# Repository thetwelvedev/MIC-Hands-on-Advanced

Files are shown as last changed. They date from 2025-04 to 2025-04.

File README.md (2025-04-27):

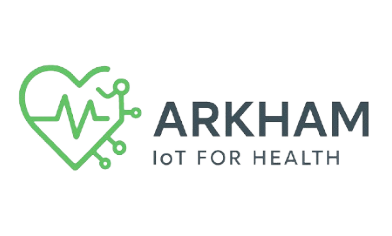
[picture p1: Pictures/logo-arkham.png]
Logo do Maloca das iCoisas
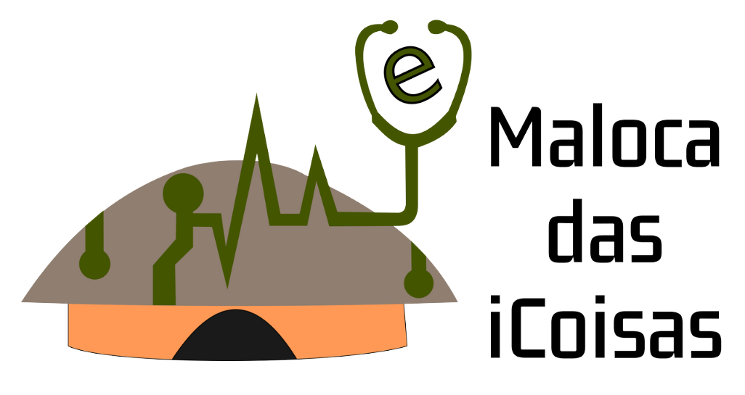
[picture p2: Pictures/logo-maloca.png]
Logo do Parceiro
#  Monitoramento de Pacientes em Situação de Risco </div>

**Componentes**: [Leonardo Castro](https://github.com/thetwelvedev), [Arthur Ramos](https://github.com/ArthurRamos26) e [Lucas Gabriel](https://github.com/lucasrocha777)

## Índice
- [Índice](#índice)
- [Etapas do Hands-on Avançado](#etapas-do-hands-on-avançado)
- [Organograma](#organograma)
- [Projeto Montado](#projeto-montado)
- [Documentos](#documentos)
  - [Big Picture](#big-picture)
  - [Documento de Requisitos Funcionais](#documento-de-requisitos-funcionais)
  - [Documento de Progresso](#documento-de-progresso)
  - [Slide do Pitch](#slide-do-pitch)
  - [Esquema de Conexões](#esquema-de-conexões)
    - [Esquema de Ligação](#esquema-de-ligação)
    - [Pinagem](#pinagem)

## Etapas do Hands-on Avançado

- [x] Sprint 0
- [x] Sprint 1
- [x] Sprint 2
- [x] Sprint 3
- [x] Apresentação - dia 25/04

## Organograma
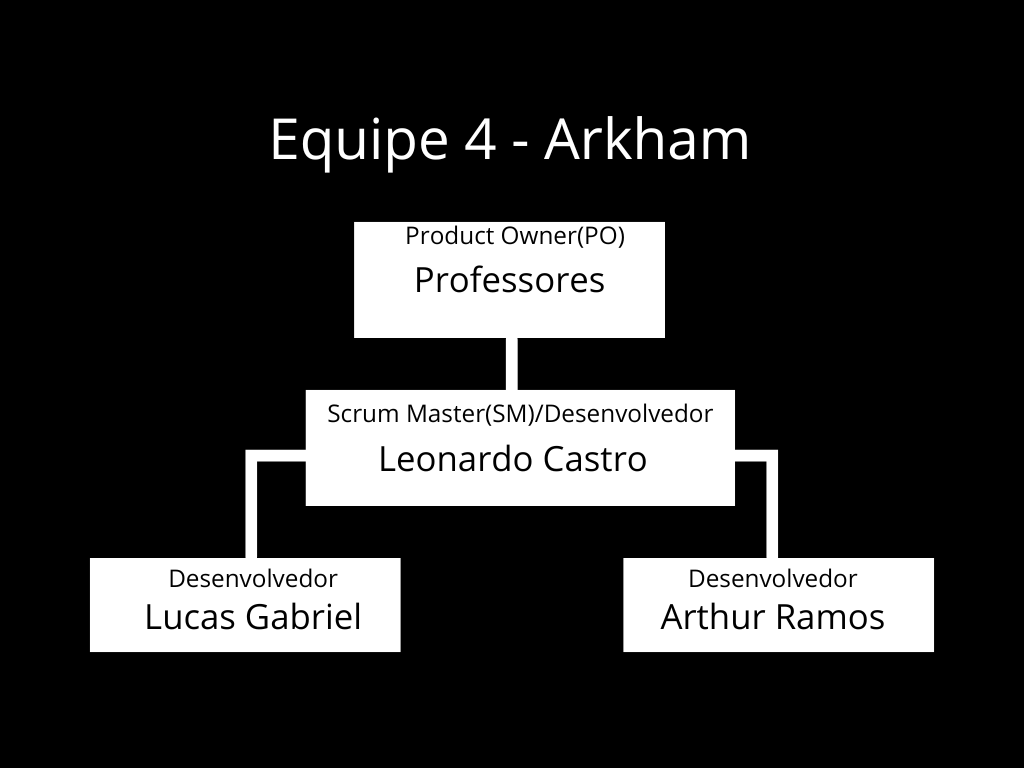
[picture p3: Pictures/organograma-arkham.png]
Organograma


## Projeto Montado
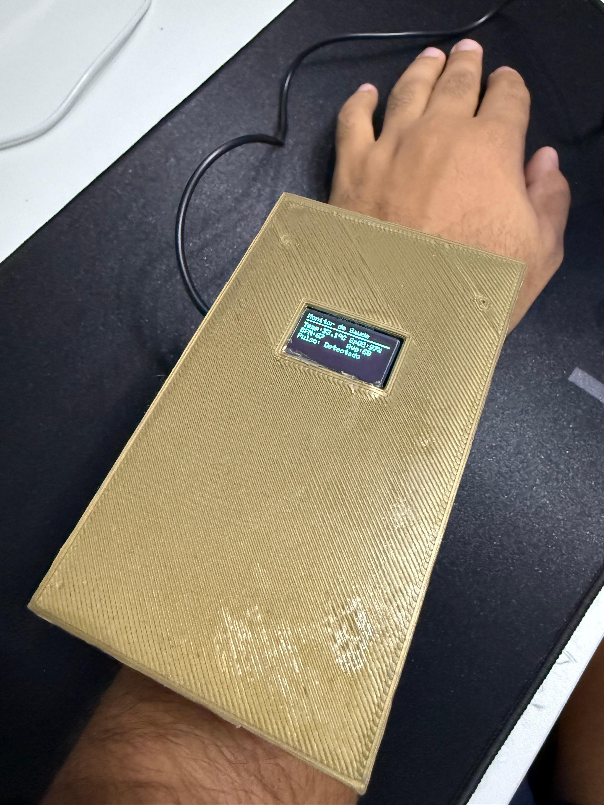
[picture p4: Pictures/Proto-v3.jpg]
Prototipo


## Documentos

### Big Picture
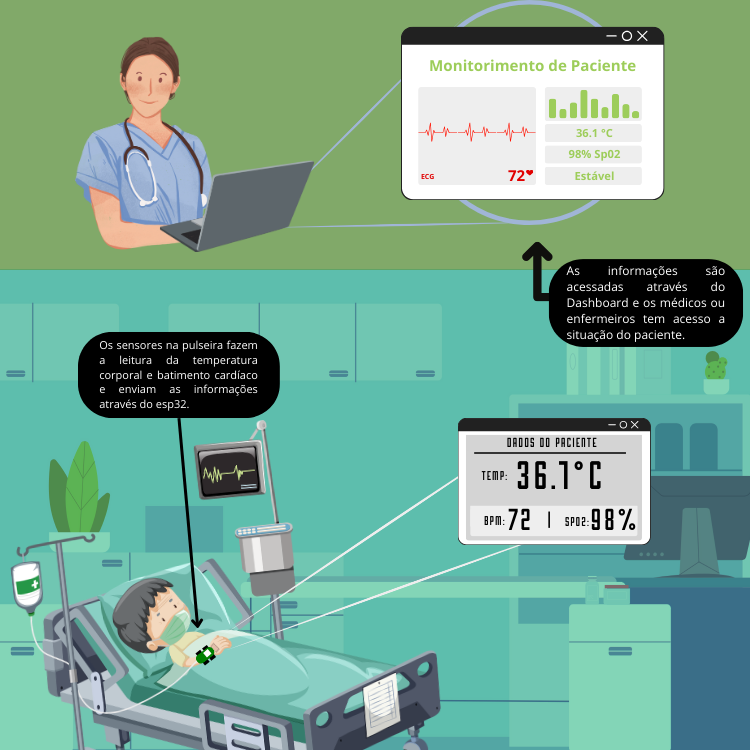
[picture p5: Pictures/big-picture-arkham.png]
Big Picture


### Documento de Requisitos Funcionais
[Acesse aqui](/Docs/Requisitos%20Funcionais_Maloca.Equipe_Arkhamdocx.pdf)

### Documento de Progresso
[Acesse aqui](/Docs/Documento%20de%20progresso%20Equipe%20Arkham.docx.pdf)

### Slide do Pitch

[Acesse aqui](/Slide/Slide%20-%20Monitoramento%20de%20Pacientes%20de%20Risco.pdf)

[Veja completo](https://www.canva.com/design/DAGlCGJqn5o/cYMYZnWsSQK9ZPAXMBt4eg/edit?utm_content=DAGlCGJqn5o&utm_campaign=designshare&utm_medium=link2&utm_source=sharebutton)

### Esquema de Conexões

#### Esquema de Ligação

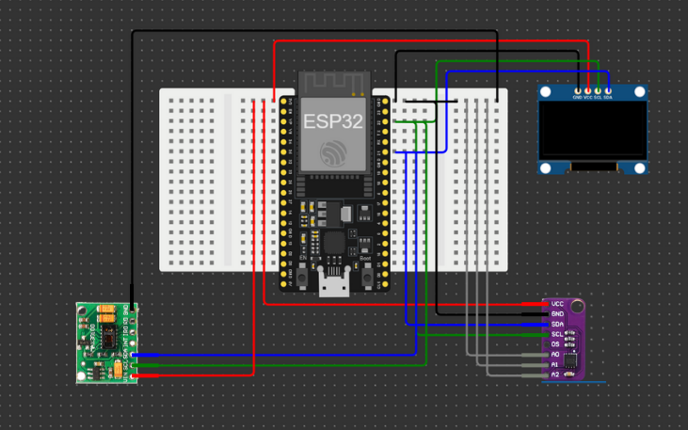
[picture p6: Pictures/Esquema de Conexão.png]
Esquema de conexão


#### Pinagem

**Conexões do MAX30102**  

| **Componente**       | **Pino ESP32** | **Descrição**                          |
|----------------------|---------------|----------------------------------------|
| **VIN (VCC)**        | 3.3V          | Alimentação (3.3V do ESP32)            |
| **GND**              | GND           | Terra (compartilhado com o ESP32)      |
| **SDA**              | GPIO21        | Dados I²C (barramento compartilhado)   |
| **SCL**              | GPIO22        | Clock I²C (barramento compartilhado)   |

**Conexões do CJMU-30205**  

| **Componente**       | **Pino ESP32** | **Descrição**                          |
|----------------------|---------------|----------------------------------------|
| **VCC**              | 3.3V          | Alimentação (3.3V do ESP32)            |
| **GND**              | GND           | Terra (compartilhado com o ESP32)      |
| **SDA**              | GPIO21        | Dados I²C (barramento compartilhado)   |
| **SCL**              | GPIO22        | Clock I²C (barramento compartilhado)   |
| **A0**               | GND           | Configura endereço I²C (padrão)        |
| **A1**               | GND           | Configura endereço I²C (padrão)        |
| **A2**               | GND           | Configura endereço I²C (padrão)        |

**Conexões do Display OLED (I²C)**  

| **Componente**       | **Pino ESP32** | **Descrição**                          |
|----------------------|---------------|----------------------------------------|
| **VCC**              | 3.3V          | Alimentação (3.3V do ESP32)            |
| **GND**              | GND           | Terra (compartilhado com o ESP32)      |
| **SDA**              | GPIO21        | Dados I²C (barramento compartilhado)   |
| **SCL**              | GPIO22        | Clock I²C (barramento compartilhado)   |

## Códigos

### Código do Circuito
```arduino
#include <WiFi.h>
#include <HTTPClient.h>
#include <Wire.h>
#include <Adafruit_GFX.h>
#include <Adafruit_SSD1306.h>
#include "MAX30105.h"
#include "heartRate.h"

// Configurações de WiFi
const char* ssid = "Nome da rede Wifi";
const char* password = "Senha";
const char* serverUrl = "http://SEU_IP_LOCAL:5000/api/data";

// Endereço I2C do MAX30205
const uint8_t MAX30205_ADDRESS = 0x48;

// Definições do display OLED
#define SCREEN_WIDTH 128
#define SCREEN_HEIGHT 64
#define OLED_RESET -1
Adafruit_SSD1306 display(SCREEN_WIDTH, SCREEN_HEIGHT, &Wire, OLED_RESET);

// Objeto do sensor de batimento
MAX30105 particleSensor;

// Buffers para leitura dos dados
#define MAX_BRIGHTNESS 255
#define BUFFER_SIZE 100
uint32_t irBuffer[BUFFER_SIZE];  
uint32_t redBuffer[BUFFER_SIZE]; 
int32_t spo2;                    
int8_t validSPO2;                
int32_t heartRate;               
int8_t validHeartRate;           

// Variáveis para cálculo de BPM
const byte RATE_SIZE = 4;
byte rates[RATE_SIZE];
byte rateSpot = 0;
long lastBeat = 0; 
float beatsPerMinute;
int beatAvg;

// Variáveis para temporização
unsigned long lastDataSend = 0;
const unsigned long SEND_INTERVAL = 2000; 

// Variável de calibração da temperatura
float calibrationOffset = 0.0;

// Protótipos de função
float readTemperature();
bool checkTempSensor();
void calibrateSensor();
void updateDisplay(float temperature, bool alert, int bpm, int avgBpm, int spo2, bool hasFinger);
void setupHeartSensor();
void readHeartRateAndSpO2();
void scanI2C();
void sendDataToServer(float temp, int bpm, int avgBpm, int spo2, bool hasFinger);
void connectToWiFi();
void reconnectWiFiIfNeeded();

void setup() {
  Serial.begin(115200);
  Wire.begin(21, 22); 

  // Inicializa o display
  if (!display.begin(SSD1306_SWITCHCAPVCC, 0x3C)) {
    Serial.println(F("Falha na inicialização do OLED"));
    while (true);
  }

  display.clearDisplay();
  display.setTextSize(1);
  display.setTextColor(SSD1306_WHITE);
  display.setCursor(0, 0);
  display.println("Inicializando...");
  display.display();

  // Conecta ao WiFi
  connectToWiFi();

  // Verifica dispositivos I2C
  scanI2C();

  // Verifica sensor de temperatura
  if (!checkTempSensor()) {
    display.clearDisplay();
    display.setCursor(0, 0);
    display.println("ERRO: Sensor temp");
    display.display();
    while (true);
  }

  calibrateSensor();     
  setupHeartSensor();   

  display.clearDisplay();
  display.setCursor(0, 0);
  display.println("Sensores prontos!");
  display.display();
  delay(1000);
}

void loop() {
  // Verifica e reconecta WiFi se necessário
  reconnectWiFiIfNeeded();

  float rawTemp = readTemperature();
  float calibratedTemp = rawTemp + calibrationOffset;
  bool overTemp = calibratedTemp >= 38.0; // Febre se >= 38 °C

  readHeartRateAndSpO2(); 

  bool hasFinger = particleSensor.getIR() > 50000;

  // Envia dados periodicamente
  if (millis() - lastDataSend > SEND_INTERVAL) {
    sendDataToServer(calibratedTemp, heartRate, beatAvg, spo2, hasFinger);
    lastDataSend = millis();
  }

  // Exibe informações no serial
  Serial.print("Temp (raw): ");
  Serial.print(rawTemp, 2);
  Serial.print(" C | Calibrada: ");
  Serial.print(calibratedTemp, 2);
  Serial.print(" C | ");
  Serial.println(overTemp ? "ALERTA: FEBRE!" : "Normal");

  Serial.print("BPM: ");
  Serial.print(heartRate);
  Serial.print(" | Média: ");
  Serial.print(beatAvg);
  Serial.print(" | SpO2: ");
  Serial.print(spo2);
  Serial.print("% | Pulso: ");
  Serial.println(hasFinger ? "Sim" : "Não");
  Serial.println("------------------------");

  updateDisplay(calibratedTemp, overTemp, heartRate, beatAvg, spo2, hasFinger);

  delay(10); 
}

// Função para ler temperatura do MAX30205
float readTemperature() {
  Wire.beginTransmission(MAX30205_ADDRESS);
  Wire.write(0x00);
  if (Wire.endTransmission(false) != 0) {
    Serial.println("Erro na comunicação com MAX30205");
    return -100;
  }

  if (Wire.requestFrom(MAX30205_ADDRESS, 2) != 2) {
    Serial.println("Dados insuficientes");
    return -100;
  }

  uint8_t msb = Wire.read();
  uint8_t lsb = Wire.read();
  
  // Verifica se os bytes são plausíveis
  if (msb == 0xFF && lsb == 0xFF) {
    Serial.println("Leitura inválida (0xFFFF)");
    return -100;
  }

  int16_t raw = (msb << 8) | lsb;
  return raw * 0.00390625; // Conversão para °C
}

// Verifica se o sensor de temperatura está presente
bool checkTempSensor() {
  Wire.beginTransmission(MAX30205_ADDRESS);
  byte error = Wire.endTransmission();
  if (error == 0) {
    Serial.println("MAX30205 detectado!");
    return true;
  } else {
    Serial.print("MAX30205 não encontrado! Erro: ");
    Serial.println(error);
    return false;
  }
}

// Calibra o sensor de temperatura
void calibrateSensor() {
  Serial.println("Calibrando temperatura... Aguarde 10s");
  display.clearDisplay();
  display.setCursor(0, 0);
  display.println("Calibrando sensor");
  display.println("Aguarde 10s...");
  display.display();
  delay(10000);

  float sum = 0;
  int validReadings = 0;
  int readings = 20;
  
  for (int i = 0; i < readings; i++) {
    float t = readTemperature();
    if (t != -100 && t > -50 && t < 100) { // Filtra valores absurdos
      sum += t;
      validReadings++;
      Serial.print("Leitura ");
      Serial.print(i);
      Serial.print(": ");
      Serial.println(t, 2);
    }
    delay(200);
  }

  if (validReadings == 0) {
    Serial.println("ERRO: Nenhuma leitura válida do sensor!");
    calibrationOffset = 0;
    return;
  }

  float avg = sum / validReadings;
  
  // Se a média estiver muito baixa (como -31.5), ajustamos para ~36°C
  if (avg < -20) {
    calibrationOffset = 36.0 - avg;
    Serial.println("Ajuste para leituras muito baixas");
  } else {
    // Caso contrário, calibramos para temperatura ambiente (~25°C)
    calibrationOffset = 25.0 - avg;
  }

  Serial.print("Média das leituras: ");
  Serial.print(avg, 2);
  Serial.print(" C | Offset calculado: ");
  Serial.print(calibrationOffset, 2);
  Serial.println(" C");
}

// Configura o sensor de batimentos cardíacos
void setupHeartSensor() {
  Serial.println("Iniciando sensor MAX30102...");

  if (!particleSensor.begin(Wire, I2C_SPEED_STANDARD)) {
    Serial.println("MAX30102 não detectado. Verifique a conexão.");
    display.clearDisplay();
    display.setCursor(0, 0);
    display.println("ERRO: Sensor cardiaco");
    display.display();
    while (1);
  }

  // Configura o sensor com os melhores parâmetros
  byte ledBrightness = 60; 
  byte sampleAverage = 4;  
  byte ledMode = 2;        
  int sampleRate = 100;    
  int pulseWidth = 411;    
  int adcRange = 4096;     

  particleSensor.setup(ledBrightness, sampleAverage, ledMode, sampleRate, pulseWidth, adcRange);
  particleSensor.enableDIETEMPRDY(); // Habilita o sensor de temperatura interna

  Serial.println("MAX30102 configurado!");
}

// Lê a frequência cardíaca e SpO2 do sensor
void readHeartRateAndSpO2() {
  long irValue = particleSensor.getIR();
  bool hasFinger = irValue > 50000;

  // Detecta batimentos cardíacos
  if (checkForBeat(irValue) {
    long delta = millis() - lastBeat;
    lastBeat = millis();

    beatsPerMinute = 60 / (delta / 1000.0);

    if (beatsPerMinute < 255 && beatsPerMinute > 20) {
      rates[rateSpot++] = (byte)beatsPerMinute;
      rateSpot %= RATE_SIZE;

      // Calcula a média dos batimentos
      beatAvg = 0;
      for (byte x = 0; x < RATE_SIZE; x++)
        beatAvg += rates[x];
      beatAvg /= RATE_SIZE;
    }
  }

  // Se não há dedo, zera os valores
  if (!hasFinger) {
    heartRate = 0;
    beatAvg = 0;
    spo2 = 0;
    validHeartRate = 0;
    validSPO2 = 0;
    return;
  }

  // Atualiza os buffers para cálculo de SpO2
  static uint32_t lastUpdate = 0;
  static int bufferIndex = 0;

  if (millis() - lastUpdate > 15) { // Coleta dados a cada 15ms
    lastUpdate = millis();
    
    redBuffer[bufferIndex] = particleSensor.getRed();
    irBuffer[bufferIndex] = irValue;
    
    bufferIndex++;
    
    if (bufferIndex == BUFFER_SIZE) {
      bufferIndex = 0;
      
      // Calcula SpO2 e BPM
      maxim_heart_rate_and_oxygen_saturation(irBuffer, BUFFER_SIZE, redBuffer, 
                                           &spo2, &validSPO2, &heartRate, &validHeartRate);
      
      // Se o cálculo de BPM falhar, usa o valor do algoritmo de batimento
      if (validHeartRate == 0 && beatAvg > 0) {
        heartRate = beatAvg;
        validHeartRate = 1;
      }
    }
  }
}

// Atualiza o display OLED
void updateDisplay(float temperature, bool alert, int bpm, int avgBpm, int spo2, bool hasFinger) {
  display.clearDisplay();
  display.setTextSize(1);
  display.setCursor(0, 0);
  display.println("Monitor de Saude");
  display.drawLine(0, 10, 127, 10, SSD1306_WHITE);

  // Temperatura
  display.setCursor(0, 15);
  display.print("Temp:");
  display.print(temperature, 1);
  display.print((char)247); // ° símbolo
  display.println("C");

  // BPM
  display.setCursor(0, 25);
  display.print("BPM:");
  if (hasFinger) {
    display.print(bpm);
  } else {
    display.print("--");
  }

  // SpO2
  display.setCursor(72, 15);
  display.print("SpO2:");
  if (hasFinger) {
    display.print(spo2);
  } else {
    display.print("--");
  }
  display.print("%");

  // Média BPM
  display.setCursor(72, 25);
  display.print("Avg:");
  if (hasFinger) {
    display.print(avgBpm);
  } else {
    display.print("--");
  }

  // Status do dedo
  display.setCursor(0, 35);
  display.print("Pulso: ");
  display.print(hasFinger ? "Detectado" : "Ausente");

  // WiFi status
  display.setCursor(0, 45);
  display.print("WiFi: ");
  display.print(WiFi.status() == WL_CONNECTED ? "Conectado" : "Desconectado");

  // Alerta de febre
  if (alert) {
    display.setCursor(0, 55);
    display.setTextColor(SSD1306_BLACK, SSD1306_WHITE);
    display.print(" ALERTA: FEBRE! ");
    display.setTextColor(SSD1306_WHITE);
  }

  display.display();
}

// Envia dados para o servidor Flask
void sendDataToServer(float temp, int bpm, int avgBpm, int spo2, bool hasFinger) {
  if (WiFi.status() == WL_CONNECTED) {
    HTTPClient http;
    
    // Cria o objeto JSON para enviar
    String httpRequestData = "{\"temperature\":" + String(temp, 2) + 
                            ",\"bpm\":" + String(bpm) + 
                            ",\"avg_bpm\":" + String(avgBpm) + 
                            ",\"spo2\":" + String(spo2) + 
                            ",\"has_finger\":" + String(hasFinger ? "true" : "false") + 
                            "}";
    
    http.begin(serverUrl);
    http.addHeader("Content-Type", "application/json");
    
    int httpResponseCode = http.POST(httpRequestData);
    
    if (httpResponseCode > 0) {
      String response = http.getString();
      Serial.println("Dados enviados com sucesso!");
      Serial.println("Resposta do servidor: " + response);
    } else {
      Serial.print("Erro no envio: ");
      Serial.println(httpResponseCode);
    }
    
    http.end();
  } else {
    Serial.println("WiFi desconectado - dados não enviados");
  }
}

// Conecta ao WiFi
void connectToWiFi() {
  Serial.println("Conectando ao WiFi...");
  display.clearDisplay();
  display.setCursor(0, 0);
  display.println("Conectando WiFi...");
  display.display();
  
  WiFi.begin(ssid, password);
  
  int attempts = 0;
  while (WiFi.status() != WL_CONNECTED && attempts < 20) {
    delay(500);
    Serial.print(".");
    display.print(".");
    display.display();
    attempts++;
  }
  
  if (WiFi.status() == WL_CONNECTED) {
    Serial.println("");
    Serial.println("WiFi conectado");
    Serial.println("Endereço IP: ");
    Serial.println(WiFi.localIP());
    
    display.clearDisplay();
    display.setCursor(0, 0);
    display.println("WiFi conectado!");
    display.print("IP: ");
    display.println(WiFi.localIP());
    display.display();
    delay(1000);
  } else {
    Serial.println("Falha na conexão WiFi");
    display.clearDisplay();
    display.setCursor(0, 0);
    display.println("Falha no WiFi!");
    display.display();
  }
}

// Verifica e reconecta WiFi se necessário
void reconnectWiFiIfNeeded() {
  if (WiFi.status() != WL_CONNECTED) {
    Serial.println("WiFi desconectado - tentando reconectar...");
    WiFi.disconnect();
    delay(100);
    connectToWiFi();
  }
}

// Scaneia dispositivos I2C
void scanI2C() {
  Serial.println("Scanning I2C...");
  byte error, address;
  int nDevices = 0;

  for (address = 1; address < 127; address++) {
    Wire.beginTransmission(address);
    error = Wire.endTransmission();

    if (error == 0) {
      Serial.print("Dispositivo encontrado: 0x");
      if (address < 16) Serial.print("0");
      Serial.println(address, HEX);
      nDevices++;
    }
  }

  if (nDevices == 0) {
    Serial.println("Nenhum dispositivo I2C encontrado!");
  }
}  
```

### Código do servidor 
```python
from flask import Flask, request, jsonify
from flask_cors import CORS
import time
from threading import Lock

app = Flask(__name__)
CORS(app)

latest_data = {
    "temperature": 0.0,
    "bpm": 0,
    "avg_bpm": 0,
    "spo2": 0,
    "has_finger": False,
    "timestamp": 0
}
data_lock = Lock()

@app.route('/api/data', methods=['POST'])
def receive_data():
    global latest_data
    try:
        data = request.get_json()
        with data_lock:
            latest_data = {
                "temperature": float(data.get('temperature', 0.0)),
                "bpm": int(data.get('bpm', 0)),
                "avg_bpm": int(data.get('avg_bpm', 0)),
                "spo2": int(data.get('spo2', 0)),
                "has_finger": bool(data.get('has_finger', False)),
                "timestamp": time.time()
            }
        return jsonify({"status": "success"}), 200
    except Exception as e:
        return jsonify({"status": "error", "message": str(e)}), 400

@app.route('/api/latest', methods=['GET'])
def get_latest_data():
    with data_lock:
        return jsonify(latest_data)

if __name__ == '__main__':
    app.run(host='0.0.0.0', port=5000, debug=True) 
```
### Código do Dashboard
```python
import streamlit as st
import requests
import time
import plotly.graph_objects as go
from datetime import datetime
import numpy as np
from pykalman import KalmanFilter

# === CONFIGURAÇÕES ===
FLASK_SERVER = "http://IP_LOCAL:5000"
UPDATE_INTERVAL = 1
MAX_RETRIES = 3

# === INICIALIZAÇÃO DO HISTÓRICO ===
if 'data_history' not in st.session_state:
    st.session_state.data_history = {
        'time': [],
        'temperature': [],
        'bpm': [],
        'filtered_bpm': [],
        'avg_bpm': [],
        'spo2': [],
        'ecg': []
    }

# === FUNÇÕES AUXILIARES ===
def fetch_data():
    for _ in range(MAX_RETRIES):
        try:
            response = requests.get(f"{FLASK_SERVER}/api/latest", timeout=2)
            if response.status_code == 200:
                data = response.json()
                data.setdefault('temperature', 0.0)
                data.setdefault('bpm', 0)
                data.setdefault('avg_bpm', 0)
                data.setdefault('spo2', 0)
                data.setdefault('has_finger', False)
                data.setdefault('ecg', generate_ecg_signal(data['bpm'] if data['has_finger'] else 0))
                return data
        except Exception as e:
            st.warning(f"Erro ao buscar dados: {str(e)}")
            time.sleep(1)
    return None

def generate_ecg_signal(bpm):
    if bpm == 0:
        return 0
    heart_rate = bpm / 60.0
    t = np.linspace(0, 1.0/heart_rate, 500)
    p_wave = 0.25 * np.sin(2 * np.pi * 5 * t) * (t < 0.2/heart_rate)
    qrs = 1.5 * np.sin(2 * np.pi * 15 * t) * ((t >= 0.2/heart_rate) & (t < 0.25/heart_rate))
    t_wave = 0.3 * np.sin(2 * np.pi * 2 * t) * ((t >= 0.3/heart_rate) & (t < 0.45/heart_rate))
    ecg = p_wave + qrs + t_wave
    return ecg[-1] + 0.05 * np.random.randn()

def moving_average(data, window=5):
    if len(data) < window:
        return data
    return np.convolve(data, np.ones(window)/window, mode='valid')

def kalman_filter(signal):
    if len(signal) < 2:
        return signal
    kf = KalmanFilter(initial_state_mean=signal[0], 
                      initial_state_covariance=1,
                      transition_matrices=[1],
                      observation_matrices=[1],
                      observation_covariance=4,
                      transition_covariance=0.1)
    filtered_state_means, _ = kf.filter(signal)
    return filtered_state_means.flatten()

# === SIDEBAR ===
with st.sidebar:
    st.image("logo-maloca.png", use_container_width=True)
    st.image("logo-arkham.png", use_container_width=True)
    st.header("Opções de Visualização")
    show_temp = st.checkbox("Temperatura", True)
    show_bpm = st.checkbox("Frequência Cardíaca", True)
    show_spo2 = st.checkbox("Oxigenação Sanguínea", True)
    show_ecg = st.checkbox("ECG", True)
    st.markdown("---")
    st.header("Filtros de Sinal")
    apply_ma = st.checkbox("Média Móvel")
    apply_kalman = st.checkbox("Filtro de Kalman")

# === LAYOUT PRINCIPAL ===
st.title('Monitor de Saúde em Tempo Real')
col1, col2, col3, col4 = st.columns(4)
temp_ph = col1.empty()
bpm_ph = col2.empty()
avg_bpm_ph = col3.empty()
spo2_ph = col4.empty()

chart_temp = st.empty() if show_temp else None
chart_bpm = st.empty() if show_bpm else None
chart_spo2 = st.empty() if show_spo2 else None
chart_ecg = st.empty() if show_ecg else None

# === LOOP PRINCIPAL ===
while True:
    data = fetch_data()
    if data:
        current_time = datetime.now().strftime("%H:%M:%S")

        st.session_state.data_history['time'].append(current_time)
        st.session_state.data_history['temperature'].append(data['temperature'])
        st.session_state.data_history['bpm'].append(data['bpm'] if data['has_finger'] else None)
        st.session_state.data_history['avg_bpm'].append(data['avg_bpm'])
        st.session_state.data_history['spo2'].append(data['spo2'])
        st.session_state.data_history['ecg'].append(data['ecg'])

        for key in st.session_state.data_history:
            max_len = 100 if key == 'ecg' else 30
            st.session_state.data_history[key] = st.session_state.data_history[key][-max_len:]

        # Aplica filtros ao BPM
        bpm_data = [x for x in st.session_state.data_history['bpm'] if x is not None]
        filtered_bpm = bpm_data

        if apply_ma:
            filtered_bpm = moving_average(filtered_bpm, window=5)
        if apply_kalman:
            filtered_bpm = kalman_filter(filtered_bpm)

        st.session_state.data_history['filtered_bpm'] = list(filtered_bpm) + [None] * (len(st.session_state.data_history['bpm']) - len(filtered_bpm))

        # === ATUALIZA MÉTRICAS ===
        temp_ph.metric("Temperatura (°C)", f"{data['temperature']:.1f}")
        bpm_ph.metric("BPM", str(data['bpm']) if data['has_finger'] else "--")
        avg_bpm_ph.metric("Média BPM", str(data['avg_bpm']) if data['has_finger'] else "--")
        spo2_ph.metric("SpO2 (%)", str(data['spo2']) if data['has_finger'] else "--")

        # === GRÁFICOS ===
        if show_temp:
            fig_temp = go.Figure()
            fig_temp.add_trace(go.Scatter(x=st.session_state.data_history['time'], y=st.session_state.data_history['temperature'], name="Temperatura", line=dict(color='orange')))
            fig_temp.update_layout(title="Temperatura Corporal", xaxis_title="Tempo", yaxis_title="°C")
            chart_temp.plotly_chart(fig_temp, use_container_width=True)

        if show_bpm:
            fig_bpm = go.Figure()
            fig_bpm.add_trace(go.Scatter(x=st.session_state.data_history['time'], y=st.session_state.data_history['bpm'], name="BPM Original", line=dict(color='blue')))
            fig_bpm.add_trace(go.Scatter(x=st.session_state.data_history['time'], y=st.session_state.data_history['filtered_bpm'], name="BPM Filtrado", line=dict(color='green', dash='dot')))
            fig_bpm.update_layout(title="Frequência Cardíaca", xaxis_title="Tempo", yaxis_title="BPM")
            chart_bpm.plotly_chart(fig_bpm, use_container_width=True)

        if show_spo2:
            fig_spo2 = go.Figure()
            fig_spo2.add_trace(go.Scatter(x=st.session_state.data_history['time'], y=st.session_state.data_history['spo2'], name="SpO2", line=dict(color='purple')))
            fig_spo2.update_layout(title="Oxigenação Sanguínea", xaxis_title="Tempo", yaxis_title="SpO2 (%)")
            chart_spo2.plotly_chart(fig_spo2, use_container_width=True)

        if show_ecg:
            fig_ecg = go.Figure()
            fig_ecg.add_trace(go.Scatter(y=st.session_state.data_history['ecg'], name="ECG", line=dict(color='red')))
            fig_ecg.update_layout(title="Eletrocardiograma (ECG)", xaxis_title="Amostras", yaxis_title="Voltagem")
            chart_ecg.plotly_chart(fig_ecg, use_container_width=True)
    else:
        st.error("Erro ao conectar com o servidor de dados.")

    time.sleep(UPDATE_INTERVAL)

```
## Configuração e Execução

### Pré-requisitos

#### Hardware:
- ESP32 com sensores conectados conforme esquema
- Computador com porta USB

#### Software:
- Python 3.8+
- Arduino IDE
- Bibliotecas Python:
```bash
pip install streamlit flask flask-cors requests plotly numpy pykalman
```

### Passo a passo

1. Configurar Ambiente:
```bash
python -m venv venv
# Linux/Mac:
source venv/bin/activate
# Windows:
venv\Scripts\activate
pip install -r requirements.txt
```

2. Executar Serviços:

- Em um terminal:
```bash
python server.py
```

- Em outro terminal:
```bash
streamlit run dashboard-tempo-real.py
```
3. Programar ESP32:
- Instale as bibliotecas necessárias na Arduino IDE:
  - Adafruit SSD1306
  - Adafruit GFX
  - MAX30105 by SparkFun
  - WiFi(No ESP32 vem por padrão)

- Carregue o código monitoramento-com-dashboard.ino

- Configure com suas credenciais WiFi

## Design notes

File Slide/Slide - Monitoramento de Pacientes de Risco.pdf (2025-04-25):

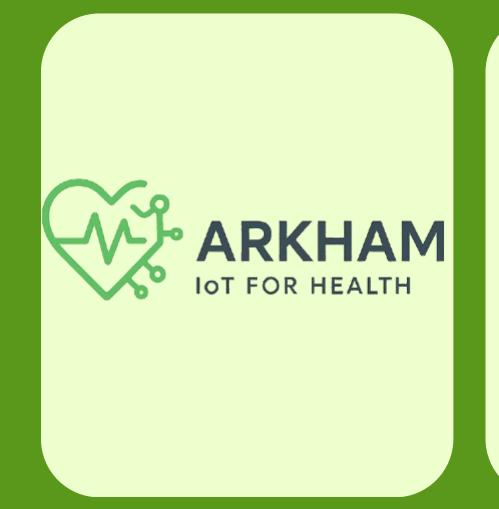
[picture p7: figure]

## E Q U I P E A R K H A M A R T H U R R A M O S L E O N A R D O C A S T R O L U C A S G A B R I E L

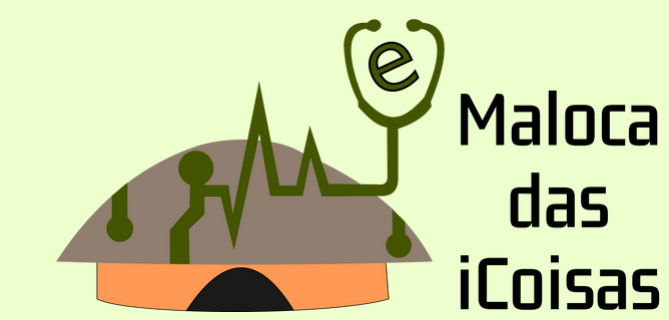
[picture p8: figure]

## L O C A L : L A B O R A T Ó R I O D O C I T D A T A : 2 5 D E A B R I L

# Monitoramento de Pacientes em Situação de Risco

## A falta de monitoramento de pacientes é um risco constante nos hospitais,podendo em casos extremos levar a óbito, os dados apurados que motivaram o trabalho foram:

## - Monitoramento contínuo reduz mortes por parada cardíaca em até

50%

## - Pacientes com sepse têm maior sobrevida se a febre for identificada e tratada nas primeiras horas - Hospitais com monitoramento contínuo têm 30% menos mortes súbita - Portanto, a falta de monitoramento aumenta riscos de óbito por

detecção tardia.

# Problema

# Solução

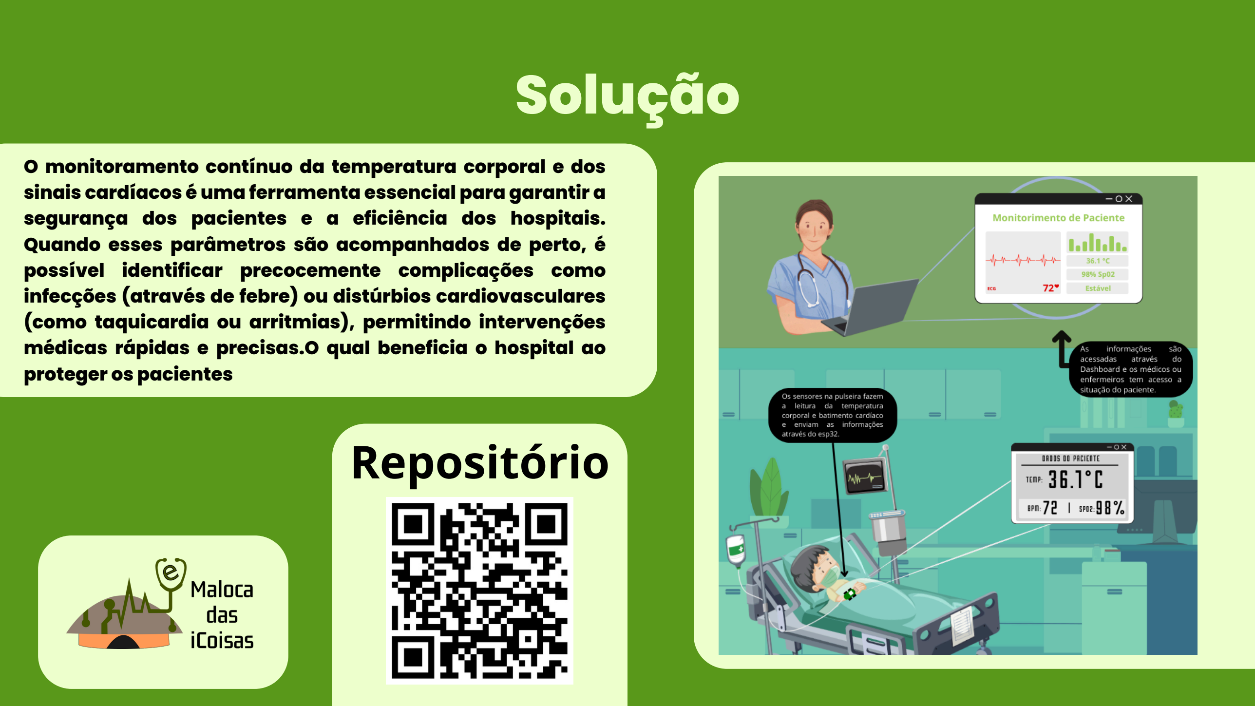
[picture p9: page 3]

### O monitoramento contínuo da temperatura corporal e dos sinais cardíacos é uma ferramenta essencial para garantir a

segurança dos pacientes e a eficiência dos hospitais.

Quando esses parâmetros são acompanhados de perto, é possível identificar precocemente complicações como infecções (através de febre) ou distúrbios cardiovasculares (como taquicardia ou arritmias), permitindo intervenções médicas rápidas e precisas.O qual beneficia o hospital ao proteger os pacientes

# Repositório

# Arquitetura

# REQUISITOS FUNCIONAIS DIAGRAMA ESQUEMÁTICO

Coleta de Dados: O sistema deve coletar dados dos sensores MAX30102 , MAX30205 em intervalos regulares
Controle Remoto dos Atuadores: O sistema deve permitir que os atuadores as notificações de aviso no site sejam acionados remotamente via sinal do ESP-32.
Comunicação de Dados: O sistema deve suportar a comunicação via Wi-Fi para envio de dados entre sensores e servidor o servidor utilizado para hospedar os dados será o firebase.

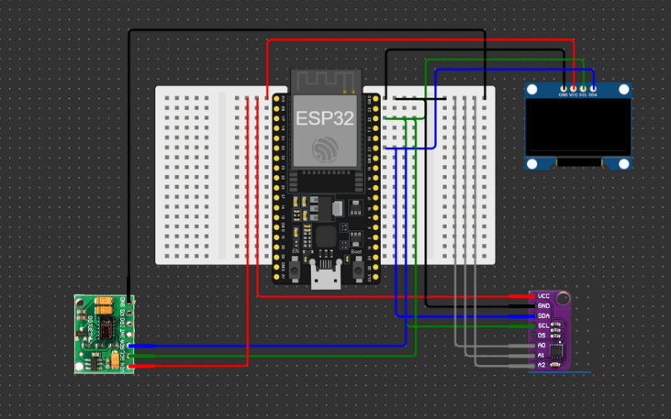
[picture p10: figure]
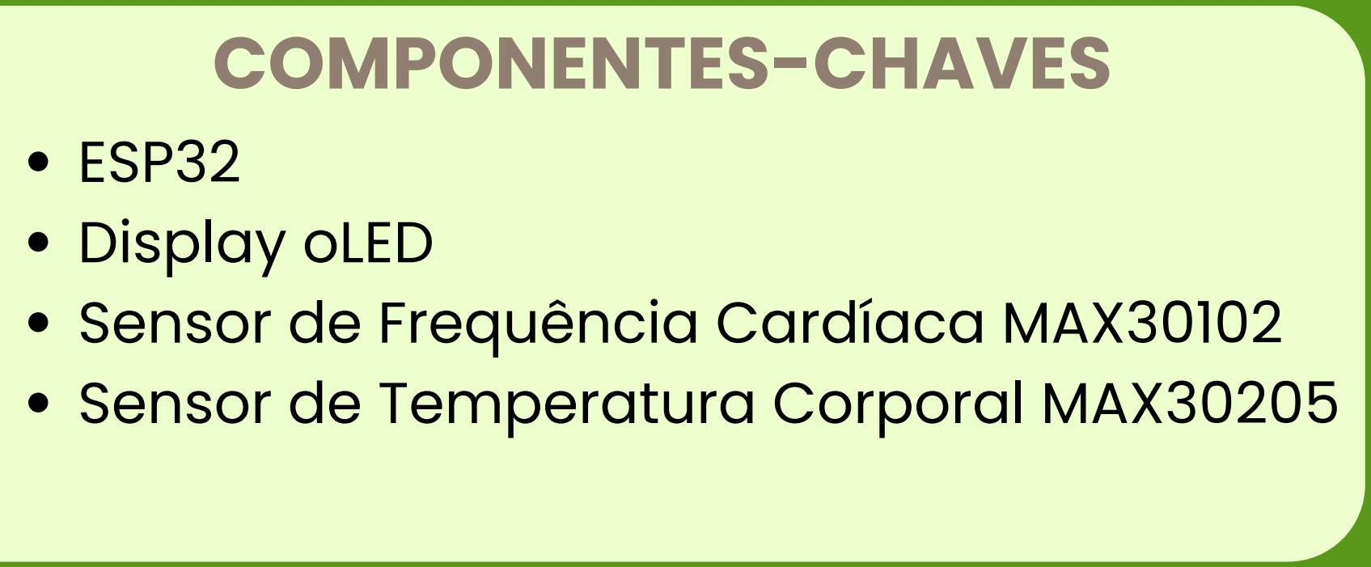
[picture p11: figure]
COMPONENTES-CHAVES ESP32 Display oLED Sensor de Frequência Cardíaca MAX30102 Sensor de Temperatura Corporal MAX30205
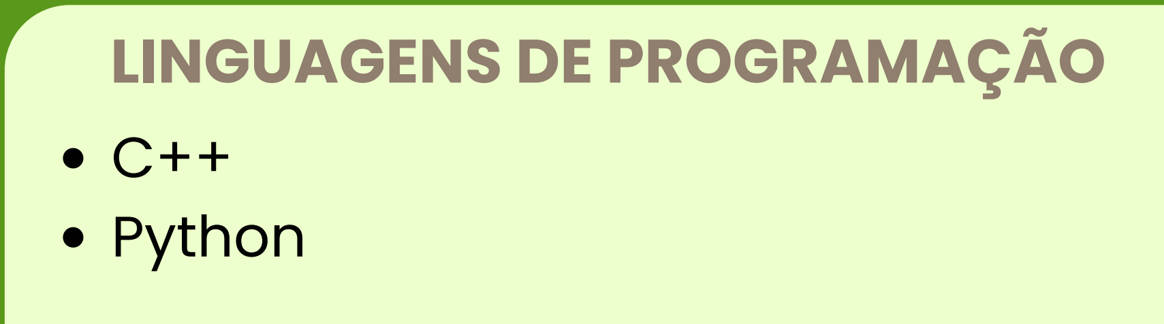
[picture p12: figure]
LINGUAGENS DE PROGRAMAÇÃO C++ Python

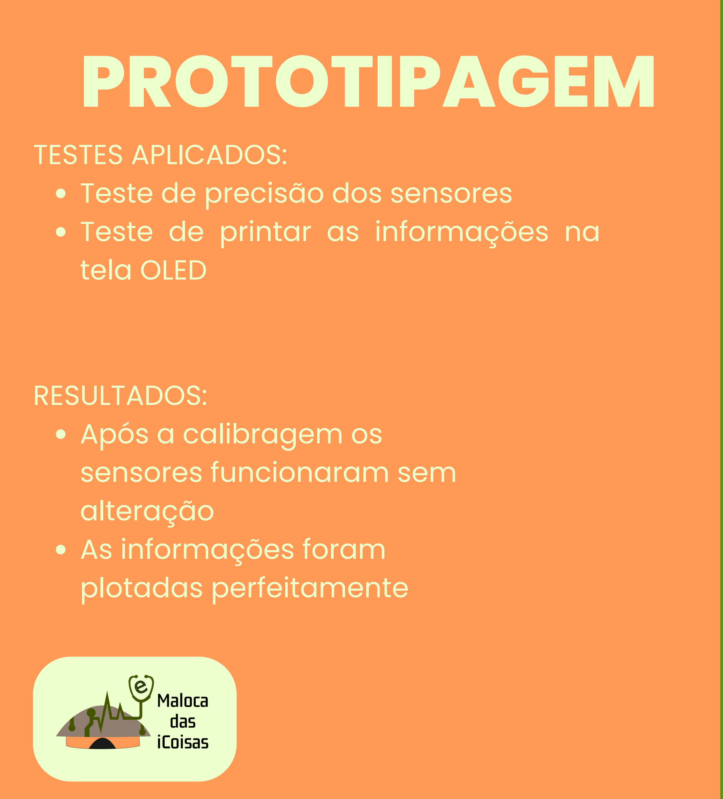
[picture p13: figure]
PROTOTIPAGEM; TESTES APLICADOS: Teste de precisão dos sensores Teste de printar as informações na tela OLED; RESULTADOS: Após a calibragem os sensores funcionaram sem alteração As informações foram plotadas perfeitamente
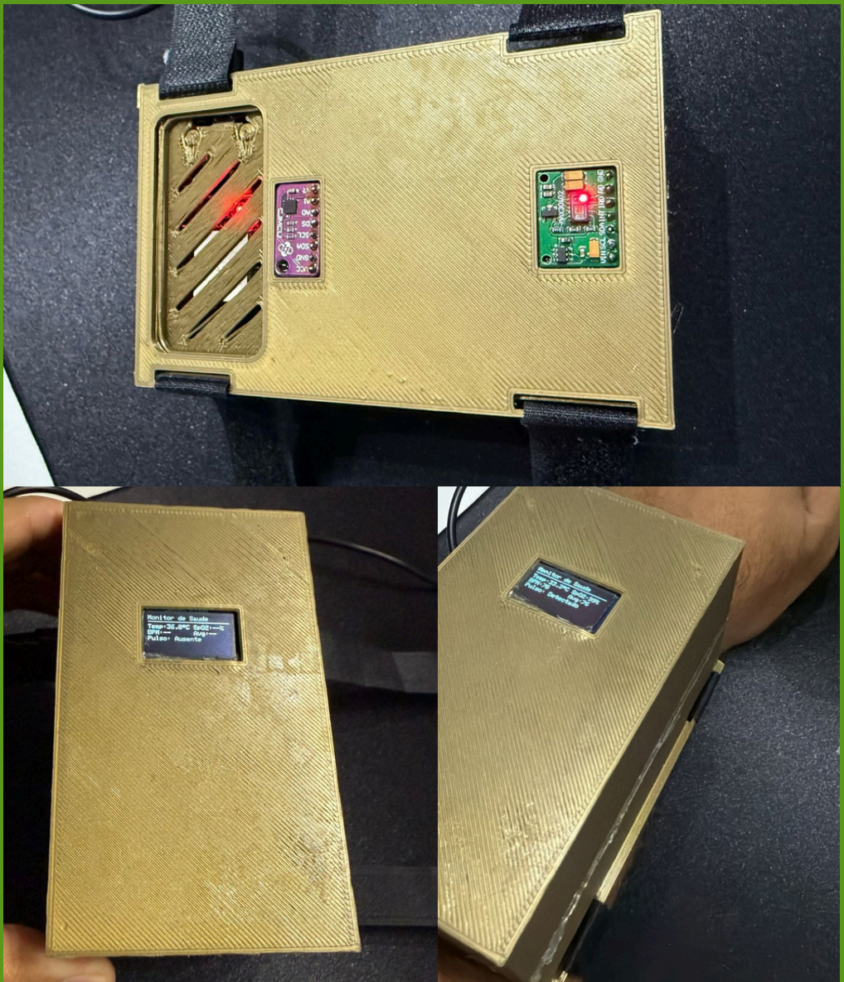
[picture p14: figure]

# Conclusão e Retrospectiva

## Histórico de Commits no GitHub

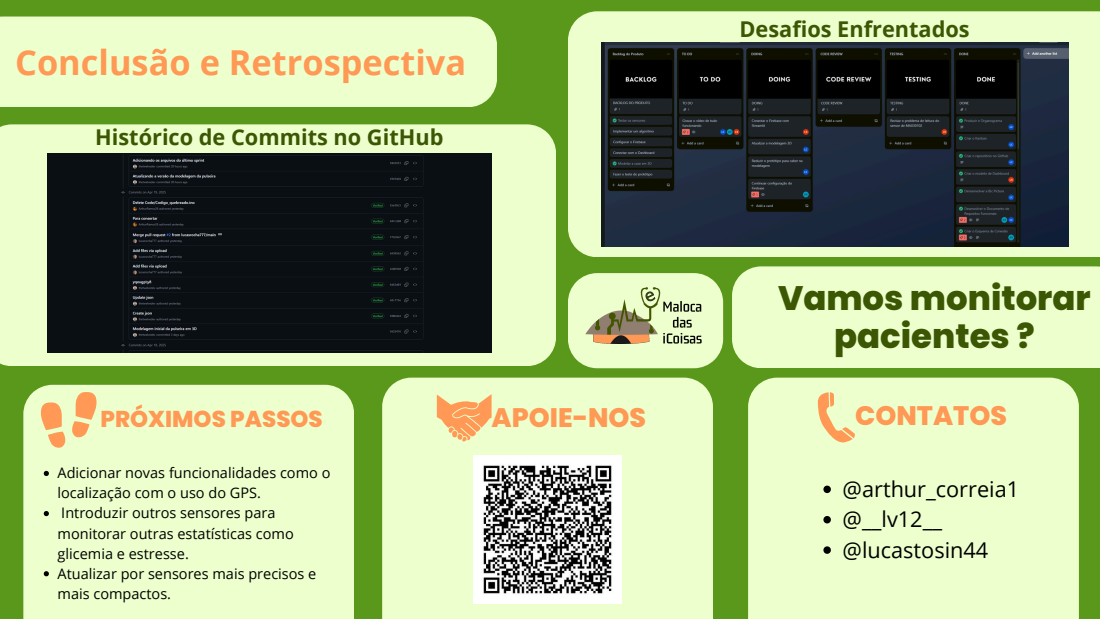
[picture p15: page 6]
PRÓXIMOS PASSOS; APOIE-NOS; CONTATOS; Vamos monitorar pacientes ?; Desafios Enfrentados; @arthur_correia1 @__lv12__ @lucastosin44

Adicionar novas funcionalidades como o
localização com o uso do GPS.
Introduzir outros sensores para
monitorar outras estatísticas como
glicemia e estresse.
Atualizar por sensores mais precisos e
mais compactos.

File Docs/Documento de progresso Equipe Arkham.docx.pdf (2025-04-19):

UNIVERSIDADE FEDERAL DE RORAIMA CENTRO DE CIÊNCIA E TECNOLOGIA DEPARTAMENTO DE CIÊNCIA DA COMPUTAÇÃO
PROJETO MALOCA DAS ICOISAS

MODELO DE DOCUMENTO DE PROGRESSO

NOME DA EQUIPE: Arkham

PARTICIPANTES: Arthur Correia De Oliveira Ramos, Leonardo Vinícius Lima Castro,

Lucas Gabriel Rocha Constancio

### 1. Informações do Projeto

- Nome do Projeto: Monitoramento de pacientes em situação de risco.
- Responsável pelo Projeto: Leonardo Vinícius Lima Castro.
- Data de Início: 11/04/2025
- Data Prevista de Conclusão: 25/04/2025
- Data do Relatório: 18/04/2025

### 2. Objetivo do Documento

Este documento visa relatar o progresso do projeto de IoT, identificando tarefas realizadas, marcos atingidos, obstáculos enfrentados e próximos passos.

### 3. Resumo

Visão geral do que foi realizado:

- Tarefas Concluídas:
- Documentação: Kanban, GitHub, Documento de requisitos funcionais, Big Picture.
- Montagem do protótipo básico.
- Código para o protótipo básico.
- Conexão Firebase.
- Dificuldades Encontradas: Conexão Firebase, Usar os dois sensores em um ESP32, desenvolvimento do dashboard.
- Soluções Adotadas: Para os sensores vamos utilizar um resistor de 4k OHMS ou 2 ESP32.

CENTRO DE CIÊNCIA E TECNOLOGIA DEPARTAMENTO DE CIÊNCIA DA COMPUTAÇÃO PROJETO MALOCA DAS ICOISAS

- Resultados e Testes:

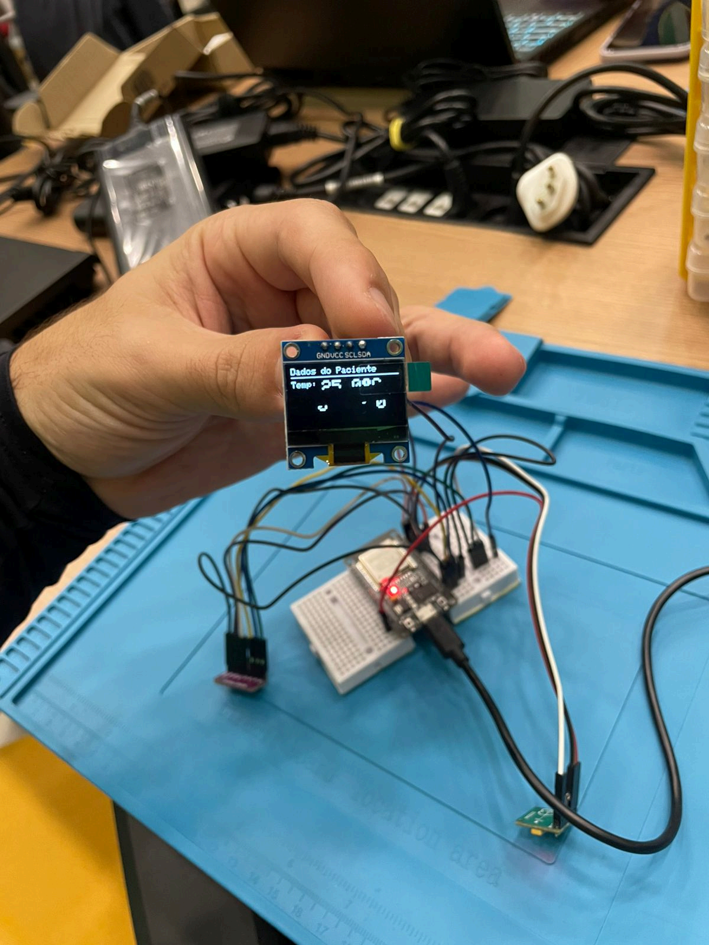
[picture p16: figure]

- Próximos Passos: Modelagem 3D para o protótipo, finalizar o dashboard, conexão dashboard com o FireBase.

### 4. Atualização Técnica

- Configuração do Hardware: Tela OLED para visualização de dados, resistor de 4k ohm.
- Configuração do Software: Melhoria no código do ESP32 para suportar os dois sensores, Melhoria no código do Dashboard.
- Integração com Serviços de Nuvem: Configurações iniciais do Firebase.
- Testes Realizados: Testamos individualmente cada sensor, testamos eles juntos mas deu erro, e testes iniciais do dashboard.

CENTRO DE CIÊNCIA E TECNOLOGIA DEPARTAMENTO DE CIÊNCIA DA COMPUTAÇÃO PROJETO MALOCA DAS ICOISAS

### 5. Riscos e Soluções

Risco Identificado | Impacto | Ações de Mitigação
Alta sensibilidade dos sensores. | Alto | Proteção dos sensores e uma conexão física estável.
Falta de espaço no protótipo 3D | Médio | Organizar a montagem do protótipo.

### 6. Observações Gerais

O processo de calibrar e testar os sensores foi de certa dificuldade, exibir os dados lidos pelos sensores e exibir no dashboard também foi dificultoso.

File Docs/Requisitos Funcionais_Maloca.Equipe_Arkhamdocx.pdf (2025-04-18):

UNIVERSIDADE FEDERAL DE RORAIMA CENTRO DE CIÊNCIA E TECNOLOGIA DEPARTAMENTO DE CIÊNCIA DA COMPUTAÇÃO PROJETO MALOCA DAS ICOISAS

Documento de Requisitos Funcionais (DRF)

NOME DA EQUIPE: Arkham
____________________________________________________________

PARTICIPANTES: Arthur Correia De Oliveira Ramos, Leonardo Vinícius Lima Castro

Lucas Gabriel Rocha Constâncio

______________________________________________________________

Esse documento visa detalhar as funcionalidades do sistema e ajudar no alinhamento entre equipe de desenvolvimento e stakeholders.

1. Introdução

1.1 Objetivo
Este documento tem como objetivo especificar os requisitos funcionais do projeto Monitoramento de pacientes de risco . Ele servirá como base para o desenvolvimento, implementação e validação do sistema.

1.2 Escopo do Projeto
O projeto Monitoramentos de pacientes de risco visa desenvolver um sistema que irá monitorar os sinais cardíacos e sinais de temperatura e em caso de alterações do mesmo utilizará strum pop-up no streamlit para avisar aos cuidadores em caso de alterações abruptas.

1.3 Definições, Acrônimos e Abreviações
- IoT: Internet das Coisas
- API: Interface de Programação de Aplicações
- UX: Experiência do Usuário
2. Descrição Geral

2.1 Perspectiva do Produto
O sistema será composto por sensores de temperatura e de batimentos cardíacos sendo: MAX30102 ,CJMCU-30205 e estará conectado a uma rede para envio de dados em tempo real e aviso caso ocorra alteração nos sinais do paciente.

2.2 Funcionalidades Principais
- Monitoramento de temperatura e sinais cardíacos .

CENTRO DE CIÊNCIA E TECNOLOGIA DEPARTAMENTO DE CIÊNCIA DA COMPUTAÇÃO PROJETO MALOCA DAS ICOISAS

- Controle remoto de sinais enviados a o servidor onde serão mostrados no streamlit.
- Interface de usuário para visualização dos dados em um site rodando localmente.
3. Requisitos Funcionais

Exemplo: Requisitos de Monitoramento

#### RF1 - Coleta de Dados

- Descrição: O sistema deve coletar dados dos sensores MAX30102 ,CJMCU-30205 em intervalos regulares.
- Prioridade: Alta
- Pré-condições: Os sensores devem estar corretamente conectados e calibrados.
- Pós-condições: Os dados coletados devem ser armazenados e enviados ao servidor.

#### RF2 - Armazenamento de Dados

- Descrição: O sistema deve armazenar os dados coletados em um banco de dados Firebase para consulta posterior.
- Prioridade: Média
- Pré-condições: Os dados devem estar organizados por carimbo de data e hora.
- Pós-condições: Dados disponíveis para visualização e análise.

#### RF3 - Controle Remoto dos Atuadores

- Descrição: O sistema deve permitir que os atuadores as notificações de aviso no site sejam acionados remotamente via sinal do ESP-32.
- Prioridade: Alta
- Pré-condições: Conexão entre o aplicativo e os atuadores.
- Pós-condições: O dispositivo responde ao comando em até 1min.

#### RF5 - Notificações de Alertas

- Descrição: O sistema deve enviar notificações ao usuário via pop-up no site e um alerta visual utilizando uma tela OLED caso alguma leitura ultrapasse um limite definido.
- Prioridade: Alta
- Pré-condições: Sistema configurado com limites para cada variável monitorada.
- Pós-condições: Notificação enviada e recebida pelo usuário.

#### RF6 - Comunicação de Dados

CENTRO DE CIÊNCIA E TECNOLOGIA DEPARTAMENTO DE CIÊNCIA DA COMPUTAÇÃO PROJETO MALOCA DAS ICOISAS

- Descrição: O sistema deve suportar a comunicação via Wi-Fi para envio de dados entre sensores e servidor o servidor utilizado para hospedar os dados será o firebase.
- Prioridade: Alta
- Pré-condições: Rede configurada e disponível.
- Pós-condições: Comunicação bem-sucedida entre os dispositivos.

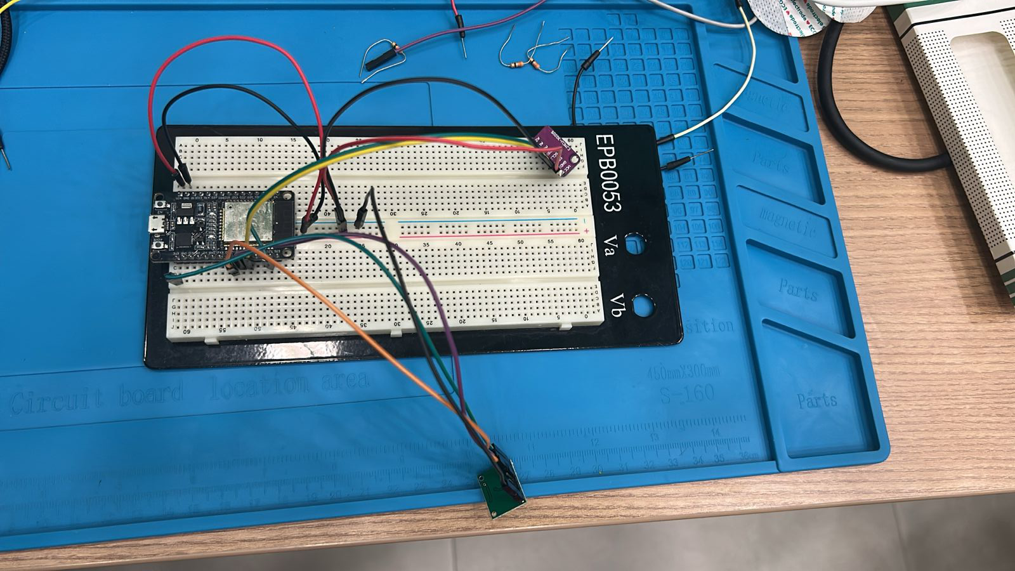
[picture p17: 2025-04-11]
Pictures/Proto-v1.jpeg

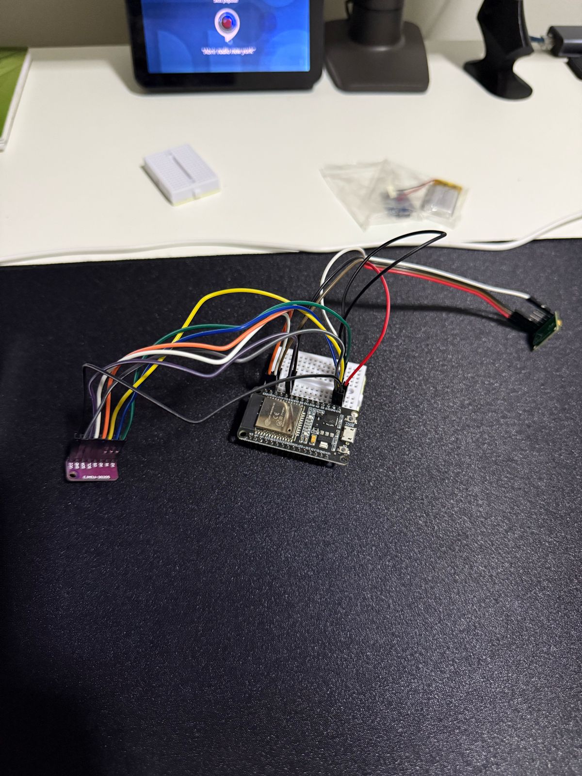
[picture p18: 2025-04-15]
Pictures/Proto-v2.jpg

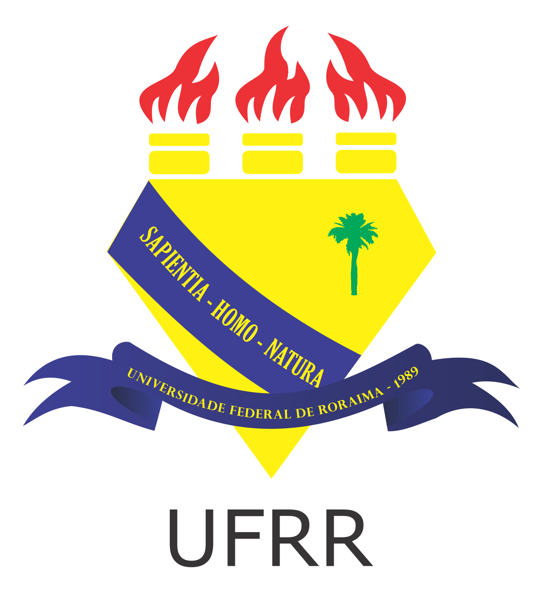
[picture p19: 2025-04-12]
Pictures/Brasão_da_UFRR.png

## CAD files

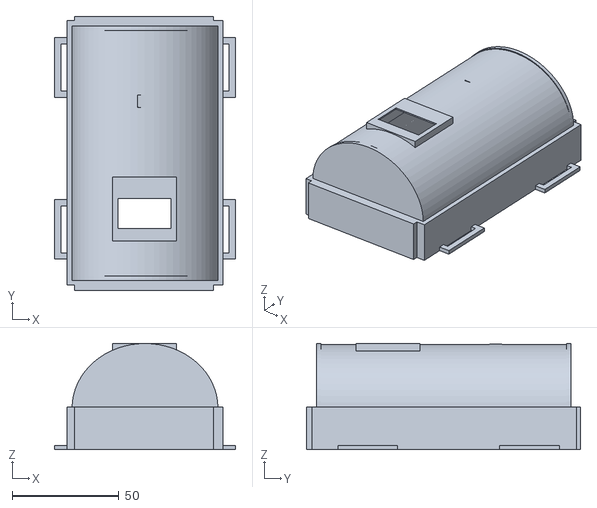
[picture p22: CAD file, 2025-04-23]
Modelagem-3D/Tampa versão final.stl
84.8 x 128.5 x 49.8

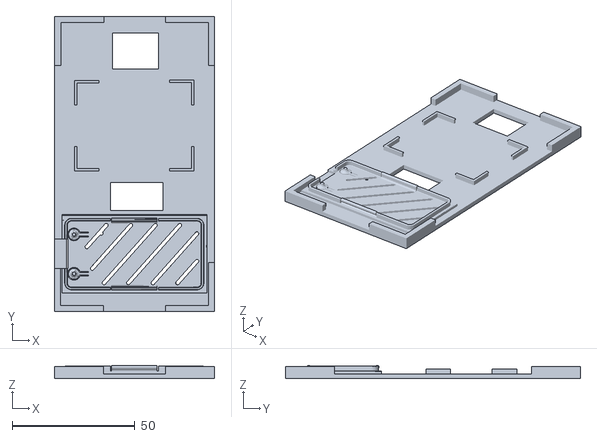
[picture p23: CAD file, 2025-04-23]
Modelagem-3D/Base versão final.stl
65.1 x 120.0 x 5.48

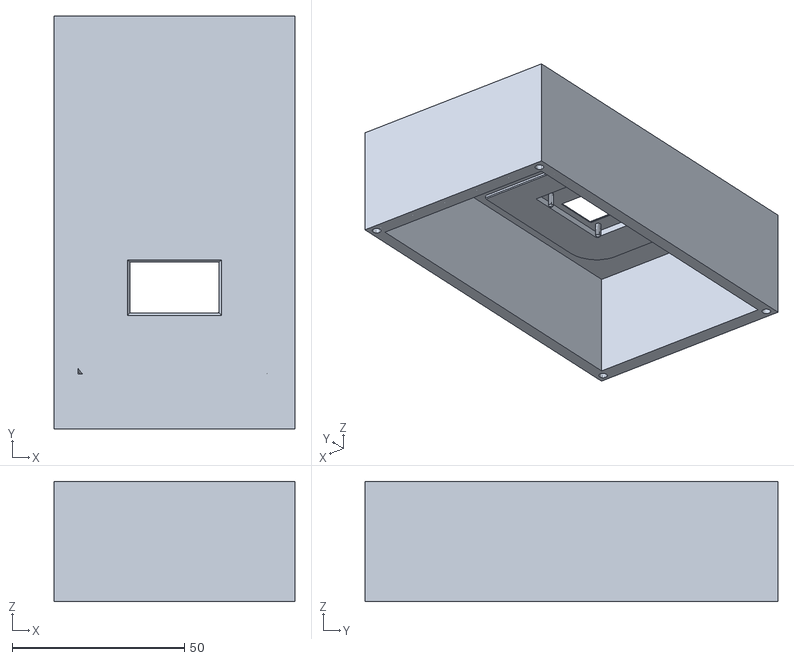
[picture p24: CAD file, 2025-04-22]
Modelagem-3D/Tampa da Pulseira Maloca v4.stl
70.0 x 120.0 x 35.0

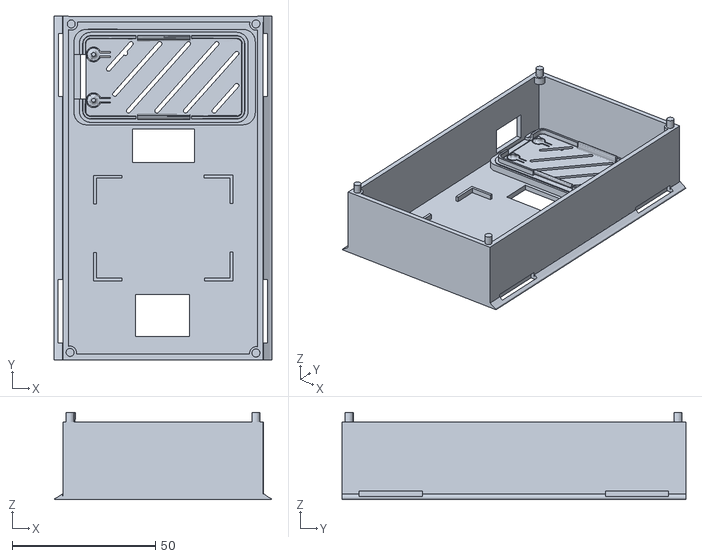
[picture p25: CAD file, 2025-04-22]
Modelagem-3D/Pulseira Maloca v4.stl
76.1 x 120.1 x 30.4

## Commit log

2025-04-11 Adicionando o arquivo do código do esp32
2025-04-11 Adiocionado o Modelo de Requisitos Funcionais sem as especificações
2025-04-11 Esquema de conexão temporário
2025-04-12 Adicionando código de teste dos componentes
2025-04-14 Adicionando o código de teste do sensor de batimento cardíaco
2025-04-14 Adicionando o código de teste do sensor de temperatura corporal
2025-04-15 Código de teste de conexão dos sensores feito
2025-04-15 Código de teste do sensor de temperatura feito
2025-04-15 Código para testar o sensor de temperatura corporal
2025-04-15 Código para testar o sensor de batimento cardíaco
2025-04-15 Update teste-max30102.ino
    Arrumadando o delay do código do sensor de batimento cardíaco
2025-04-17 Código com os últimos testes dos sensores
2025-04-17 Fazendo o teste de código para solucionar o problema de leitura do batimento cardiaco
2025-04-18 Código para encontrar os endereços dos dispositivos que usam o barramento I2C
2025-04-19 Atualizando o README.md e adicionando esquema de conexão
2025-04-19 Adicionando o artefato de 18 de abril
2025-04-19 Modelagem inicial da pulseira em 3D
    [Parte de Baixo Pulseira Maloca V1.stl, Parte de Cima Pulseira Maloca V1.stl, Tampa de Baixo do Oled Maloca V1.stl]
2025-04-20 Atualizando a versão da modelagem da pulseira
    [Parte de Baixo Pulseira Maloca V1.stl, Parte de Cima Pulseira Maloca V1.stl, Pulseira Maloca v3.stl, Tampa de Baixo do Oled Maloca V1.stl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]
2025-04-22 Removendo modelagem antiga
    [Pulseira Maloca v3.stl, Teste de base da Pulseira Maloca v2.1.stl]
2025-04-22 Atualizando o código do protótipo
    [Tampa esp32.stl]
2025-04-22 Adicionando as novas modelagens 3D
    [Pulseira Maloca v4.stl, Tampa da Pulseira Maloca v4.stl]
2025-04-22 Novo código do esp32 de teste
2025-04-23 Novo arquivo Teste
    Nesse arquivo teste foi implementado o algoritmo de filtragem de ruído.
2025-04-23 Adicionando as novas modelagens
    [Base versão final.stl, Tampa versão final.stl]
2025-04-23 Código que roda todos os sensores sem o firebase
2025-04-23 Código inicial de testes
2025-04-25 Removendo os códigos de teste e desenvolvimento antigo
2025-04-25 Adicioando o código do servidor usando o flask para intermediar a comunicação do eps32 com o streamlit
2025-04-25 Adicionando o código do esp32 em que todos os sensores estão funcionando e ele envia os dados para o servidor flask usando json
